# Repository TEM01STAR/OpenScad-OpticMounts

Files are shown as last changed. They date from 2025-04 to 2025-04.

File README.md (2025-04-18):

# OpenScad-OpticMounts
This is a work in progress collection of 3d printable optic table mounts. They are written in OpenScad, not because I am good at using it, but because it is open source. The code will likely be messy, be warned.

## Design intentions:
1. Keep the cost low.
2.  Be compatible with existing optical setups where possible.
3.   Be as precise as possible without violating 1 and 2 ;)

Where possible, all hardware has been parameterized so the models can be tweaked to your preferences. The default models are using metric fasteners in sizes that work with the normal U.S. standard of 1 inch diameter optics and an optical bench consisting of 1/4-20 tapped holes on a 1 inch grid. Yes, this is cursed, but I prefer to stock metric fasteners.

Cover Image

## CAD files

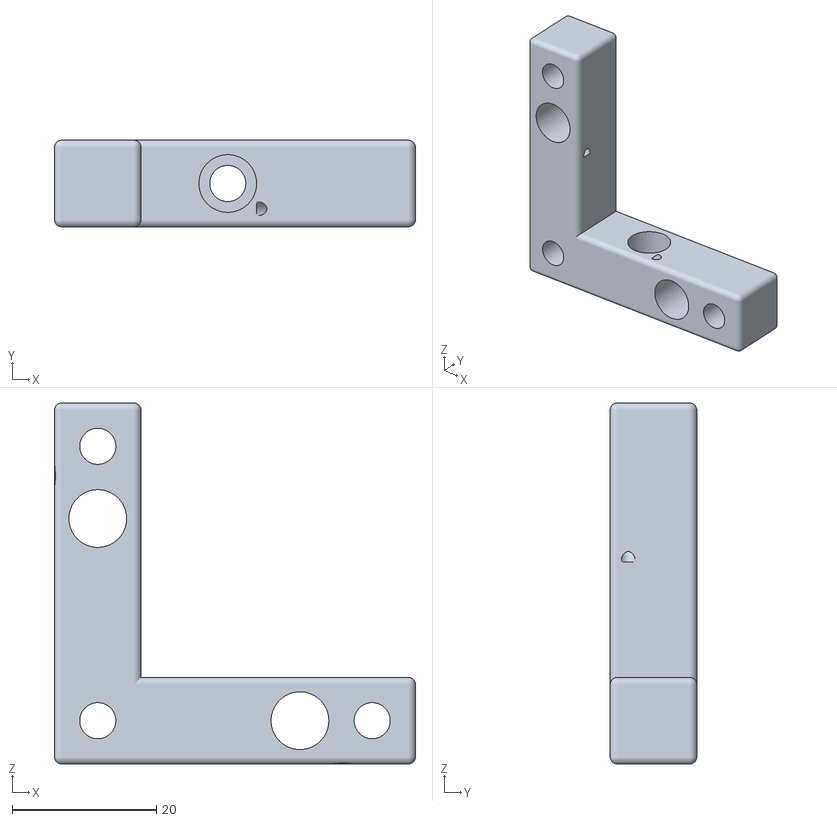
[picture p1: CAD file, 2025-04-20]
STLs/TipTiltBase_4-9-25_V1.stl
50.0 x 12.0 x 50.0

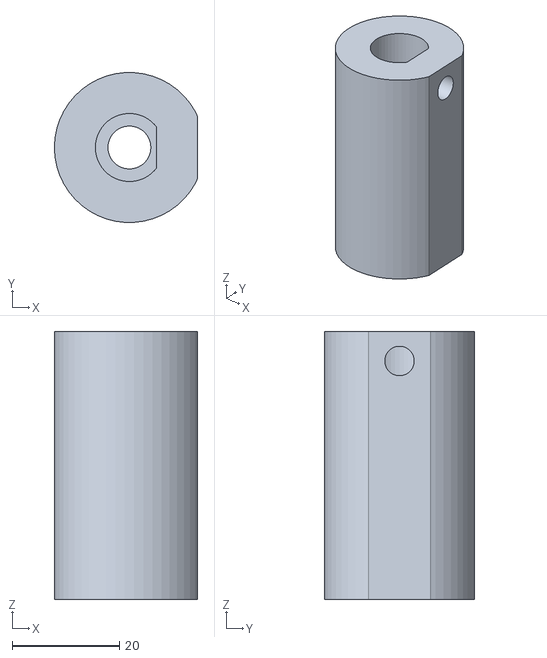
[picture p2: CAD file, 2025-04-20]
STLs/PrintedSocket4-11-25_V1.stl
26.7 x 27.9 x 50.0

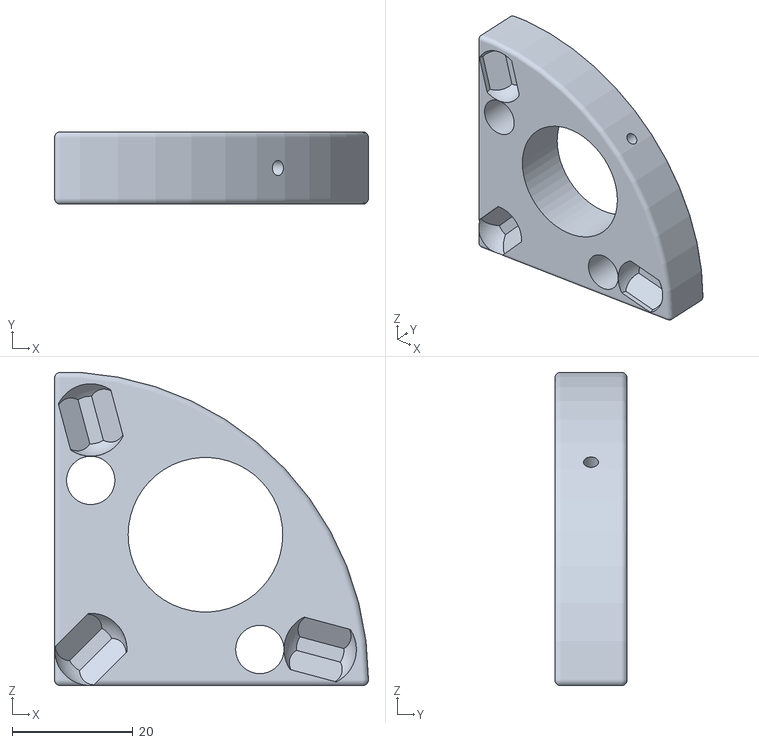
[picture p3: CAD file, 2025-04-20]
STLs/TipTiltCircleMount_4-9-25_V1.stl
52.0 x 12.0 x 51.9

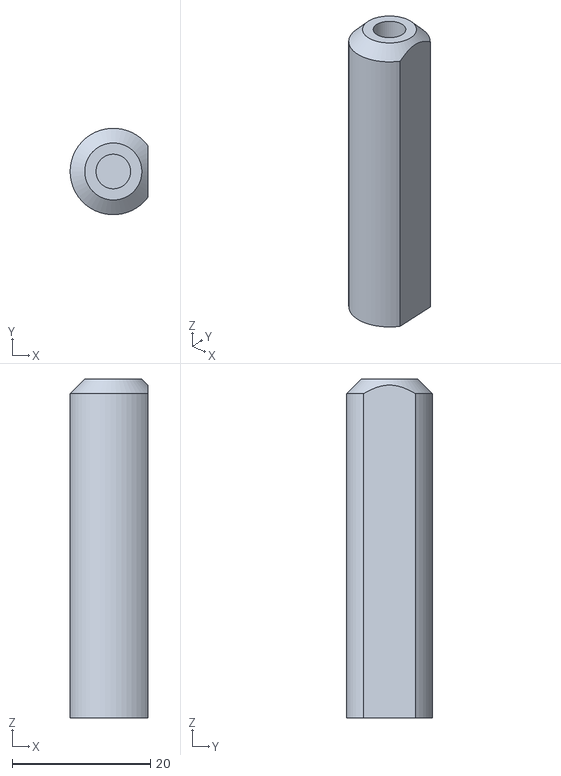
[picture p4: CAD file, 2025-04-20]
STLs/PrintedPost4-11-25_V1.stl
11.2 x 12.5 x 49.0

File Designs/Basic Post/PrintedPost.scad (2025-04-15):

//A Optics Post mount, loosely based on the conventional post in tube style seen in most optical systems.
//Author TEM01*

$fn = 50;

/*[General Parameters]*/
//Generate the "Post", the "Socket", or "Both" components.
generate = "Both";
//Clearance is used for fillets and clearance between moving parts. It is intended to be 1mm.
clearance = 1;
//Tolerance is used for printer tolerancing for snug fit parts
tolerance = 0.1;

/*[Hardware Parameters]*/
//Top post connection type "Heatset" or "Threaded" Threaded not implemented yet
top_thread = "Heatset";
//Top post heatset diameter
top_hsert_dia = 5;
//Top post heatset depth
top_hsert_depth = 12;

//Bottom Socket connection type "Heatset" or "Threaded" Threaded not implemented yet
bot_thread = "Heatset";
//Bottom post heatset diameter
bot_hsert_dia = 8;
//Bottom post heatset depth
bot_hsert_depth = 8;

//Post Height
post_height = 50;
//Post Diameter
post_dia = 12.5;

//Socket Height
socket_height = 50;
//Socket Outer Diameter
socket_dia = 28;

//Key type. Currently only "Flat" or "None"
key = "Flat";

//Fixing Bolt Hole Diameter
fix_hole = 5.5;

if(generate == "Post"){Post();}
else if(generate == "Socket"){Socket();}
else if(generate == "Both"){
    translate([0,0,0]){
        Socket();
    }
    translate([0,0,bot_hsert_dia]){
        Post();
    }
}

module Post(){
    difference(){
        union(){
            intersection(){
                PostOrSocketHole(post_height,post_dia);
                translate([0,0,post_height-post_dia/4]){
                    cylinder(h = post_dia/4-clearance, d1 = post_dia, d2 = post_dia-post_dia/2+2*clearance);
                }
            }
            PostOrSocketHole(post_height-post_dia/4,post_dia);
        };
        translate([0,0,post_height-top_hsert_depth]){
            cylinder(top_hsert_depth,d=top_hsert_dia);
        }
    }
}

module Socket(){
    difference(){
        cylinder(socket_height, d = socket_dia);
        translate([0,0,bot_hsert_dia]){
            PostOrSocketHole(post_height,post_dia+2*tolerance);
        }
        cylinder(bot_hsert_depth, d = bot_hsert_dia);
        translate([0,0,socket_height-fix_hole]){
            rotate([0,90,0]){
                cylinder(socket_dia, d = fix_hole);
                translate([0,0,socket_dia/2.2]){
                    cylinder(socket_dia, d = 2*socket_height);
                }
            }
        }
    }
}

module PostOrSocketHole(height, diameter){
    difference(){
        cylinder(height, d = diameter);
        if(key == "Flat"){
            translate([0.4*diameter,-0.5*diameter,0]){ //flat is 90% of the circle
                cube([diameter,diameter,height]);
            }
        }
    }
}

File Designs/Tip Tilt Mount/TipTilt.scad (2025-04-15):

//Tip/Tilt stage, Author TEM01*
//A WIP basic tip/tilt kinematic mount for 3d printing optical equipment. Intent is low cost, "educational grade".
//Using M3 threaded balls interfacing with 3d printed slopes for a kinematic mount. This is not perfect, as the printed surfaces tend to have stiction problems, along with creep and wear. The threaded balls in a maxwellian mount was inspired by Joshua Vasquez's Jubilee 3d printer toolchanging project. In his case, using inserted metal rods solved this problem. something to think about. 3-30-25
//Further thoughts on precision, as I test this rewrite. This will never have the perfect smooth motion that the machined versions do, but thats okay, as long as once something is adjusted it stays there and the adjustment is intuitive enough that the human copntrol loop doesn't get frustrated. With this in mind, the most stable version of this mount is a 120° even angular separation maxwell kinematic mount. I will leave the much smoother operating kelvin mount in this code, but I think its sensitivity to print tolerances and vibration make it ill advised. A modification for future stability would be to replace the center pivot of a maxwellian mount with a 3DOF socket, although that is technically an overconstraint. 4-7-25
//Rewritten in OpenScad for easier distribution. This is not a program I am familiar with yet, so it will be messy.

$fn = 50;

/*[General Parameters]*/
//Generate the "TiltBase", the "OpticMount", or "Both" components.
generate = "Both";
//Clearance is used for fillets and clearance between moving parts. It is intended to be 1mm.
clearance = 1;
//Tolerance is used for printer tolerancing for snug fit parts
tolerance = 0.1;
//Width is the overall x/y width of the optical mount.
Width = 50;
//Thickness is the z thickness of each part.
Thickness = 12;

/*[Hardware Parameters]*/
//Diameter of the balls used for the coupling
kinematic_ball_diameter = 8;
//Heated insert diameter for the kinematic. Set to the thread diameter if you prefer to directly tap the plastic.
kinematic_thermal_insert_diameter = 5;
//Spring Diameter
spring_diameter = 8;
//Spring distance from center
spring_offset = 28;
//Spring retention pin diameter
spring_pin = 2;
//Spring pin head
spring_pin_head = 4;
//Mounting through hole - 5mm for a 10-32 screw
mount_bolt_hole = 5;
//Bolt head cutout
mount_bolthead_hole = 8;
//Bolt Location
mount_location = 24;

/*[Optic Mount Parameters]*/
//Currently only "Circle", "Plate", or "None"
optic_style = "Circle";
optic_diameter = 25.5;
//Type of kinematic coupling. "Kelvin" or "Maxwell"
kinematic_style = "Maxwell";


if(generate == "TiltBase"){TiltBase(Width,Thickness);}
else if(generate == "OpticMount"){OpticMount(Width,Thickness);}
else if(generate == "Both"){
    translate([0,-Thickness,0]){
        TiltBase(Width,Thickness);
    }
    translate([0,Thickness,0]){
        OpticMount(Width,Thickness);
    }
}

module TiltBase(width, thi){
    difference(){
        minkowski(){
            union(){
                cube([width-2*clearance,thi-2*clearance,thi-2*clearance]);
                cube([thi-2*clearance,thi-2*clearance,width-2*clearance]);
            }
            translate([1,1,1]){
                sphere(clearance);
            }
        };
        //Insert Holes
        translate([thi/2,0,thi/2]){
            rotate([-90,0,0]){
                cylinder(thi,d=kinematic_thermal_insert_diameter);
            }
        }
        translate([thi/2,0,width-thi/2]){
            rotate([-90,0,0]){
                cylinder(thi,d=kinematic_thermal_insert_diameter);
            }
        }
        translate([width-thi/2,0,thi/2]){
            rotate([-90,0,0]){
                cylinder(thi,d=kinematic_thermal_insert_diameter);
            }
        }
        //Spring Holes
        translate([thi/2,0,spring_offset+thi/2]){
            rotate([-90,0,0]){
                cylinder(thi,d=spring_diameter);
            }
        }

        translate([spring_offset+thi/2,0,thi/2]){
            rotate([-90,0,0]){
                cylinder(thi,d=spring_diameter);
            }
        }
        SpringPins(thi);
        //Mounting Hole
        translate([mount_location,thi/2,0]){
            union(){
                cylinder(thi,d=mount_bolt_hole);
                translate([0,0,thi/2]){
                    cylinder(thi/2,d=mount_bolthead_hole);
                }
            }
        }  
    }
}


module OpticMount(width, thi){
    difference(){
        if(optic_style == "Circle"){CircleMount(width,thi);}
        else if(optic_style == "Plate"){PlateMount(width,thi);}
        else if(optic_style == "None"){BasicMount(width,thi);}

        if (kinematic_style == "Kelvin") {KelvinNegatives(width,thi);}
        else if(kinematic_style == "Maxwell") {MaxwellianNegatives(width,thi);}
        //Spring Holes
        translate([thi/2,0,spring_offset+thi/2]){
            rotate([-90,0,0]){
                cylinder(thi,d=spring_diameter);
            }
        }
        translate([spring_offset+thi/2,0,thi/2]){
            rotate([-90,0,0]){
                cylinder(thi,d=spring_diameter);
            }
        }
        translate([0,thi/2,0]){
            SpringPins(thi);
        }
    }
}
module OneDOF(){
    rotate([-90,0,0]){
        cylinder(kinematic_ball_diameter,d=kinematic_ball_diameter+clearance,center=true);
    }
}

module TwoDOF(){
    rotate([0,45,0]){
        rotate([0,0,45]){
            intersection(){
                intersection(){
                    rotate([0,0,45]){
                        cube([kinematic_ball_diameter+1,kinematic_ball_diameter+1,3*kinematic_ball_diameter],center=true);
                    }
                    cube([kinematic_ball_diameter,kinematic_ball_diameter,3*kinematic_ball_diameter],center=true);
                }
                sphere(d=kinematic_ball_diameter+4*clearance);
            }
        }
    }
}

module ThreeDOF(){
    union(){
        sphere(kinematic_ball_diameter/2);
        rotate([-90,0,0]){
            translate([0,0,kinematic_ball_diameter/2]){
                cylinder(2,d=kinematic_ball_diameter-clearance,center=true);
            }
        }
    }
}

module MaxwellianNegatives(width,thi){
    translate([thi/2,0,thi/2]){
        TwoDOF();
    }
    translate([thi/2,0,width-thi/2]){
        rotate([0,120,0]){
            TwoDOF();
        }
    }
        translate([width-thi/2,0,thi/2]){
        rotate([0,-120,0]){
            TwoDOF();
        }
    }
}

module KelvinNegatives(width,thi){
    translate([thi/2,0,thi/2]){
        ThreeDOF();
    }
    translate([thi/2,0,width-thi/2]){
        OneDOF();
    }
        translate([width-thi/2,0,thi/2]){
        rotate([0,-90,0]){
            TwoDOF();
        }
    }
}

module CircleMount(width,thi){
    difference(){
        minkowski(){
            union(){
                cube([width-2*clearance,thi-2*clearance,thi-2*clearance]);
                cube([thi-2*clearance,thi-2*clearance,width-2*clearance]);
                intersection(){
                    rotate([-90,0,0]){
                            cylinder(thi-2*clearance,r=width);
                    }
                    cube([width,thi-2*clearance,width]);
                }
            }
            translate([1,1,1]){
                sphere(clearance);
            }
        };
        translate([width/2,0,width/2]){
            rotate([-90,0,0]){
                cylinder(thi,d=optic_diameter+tolerance);
            }
        }
        translate([width/2,thi/2,width/2]){
            rotate([0,45,0]){
                cylinder(width,d=2.5);
            }
        }
    }
}

module PlateMount(width,thi){
    cube([width,thi,width]);
}

module BasicMount(width,thi){
    minkowski(){
        union(){
            cube([width-2*clearance,thi-2*clearance,thi-2*clearance]);
            cube([thi-2*clearance,thi-2*clearance,width-2*clearance]);
        }
        translate([1,1,1]){
            sphere(clearance);
        }
    } 
}

module SpringPins(thi){
    translate([spring_offset+thi,spring_pin/2+1.5,0]){
        rotate([0,-45,0]){
            cylinder(thi*2.828,d=spring_pin,center=true);
        }
    }
    translate([0,spring_pin/2+1.5,spring_offset+thi]){
        rotate([0,-45,0]){
            cylinder(thi*2.828,d=spring_pin,center=true);
        }
    }
    translate([spring_offset+thi,spring_pin/2+1.5,0]){
        rotate([0,-45,0]){
            cylinder(spring_pin_head,d=spring_pin_head,center=true);
        }
    }
    translate([0,spring_pin/2+1.5,spring_offset+thi]){
        rotate([0,-45,0]){
            cylinder(spring_pin_head,d=spring_pin_head,center=true);
        }
    }
}

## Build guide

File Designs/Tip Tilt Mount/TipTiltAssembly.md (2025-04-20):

# Tip Tilt Optical Mount

## Bill of Materials

|Part Type         |Quantity|Default Size           |Approximate Price April 2025|
|------------------|--------|-----------------------|----------------------------|
|Tooling Balls     |3       |8mm Dia M3 Thread      |$1.8                        |
|Adjustment Screws |3       |M3x20 Socket Head      |$0.3                        |
|Adjustment Heatset|3       |M3 5mm Dia 8mm Long    |$0.6                        |
|Springs           |2       |5mm Dia 20mm Ext Spring|$2.0                        |
|Spring Pins       |4       |M2x12mm Socket Head    |$1.2                        |
|Printed Parts     |20g     |Carbon fiber PLA       |$1.6                        |

Total approximate price is $7.5, which is more reasonable for educational settings than $50+ for commercial versions.
Of course, commercial mounts are far more stable, but that's the tradeoff.

##Assembly Pictures
0Parts

Install the heatset inserts as perpendicular as possible, it is critical to smooth motion of the final assembly. The spring prins should be the closest to the top.
1Heatsert

Install the positioning screws from the same side as the heatserts.
2PosScrews

Add the tooling balls.
3Balls

Install the springs to the back 3d print by passing the pins through the loop of the spring.
4BackSprings

The most difficult part - Pull the extension springs into the front half of the print, and install the pins through the loops. This is easier to do with forceps or needlenose pliers. Using thread or fishing line is also a good way to assemble them.
5FrontSprings

All Done:
6Finished

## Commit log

2025-04-10 Added the Tip/Tilt Stage. First file released!
    [TipTilt.scad]
2025-04-15 Improved tolerances on the Tip Tilt mount, added a very simple printed post.
    [PrintedPost.scad, TipTilt.scad]
2025-04-18 Adding assembly instruction for tip-tilt mount.
    [PrintedPost.scad, TipTilt.scad]
2025-04-18 Messed up prev commit
    [PrintedPost.scad, TipTilt.scad]
2025-04-20 Added V1 STLs
    [PrintedPost4-11-25_V1.stl, PrintedSocket4-11-25_V1.stl, TipTiltBase_4-9-25_V1.stl, TipTiltCircleMount_4-9-25_V1.stl]
